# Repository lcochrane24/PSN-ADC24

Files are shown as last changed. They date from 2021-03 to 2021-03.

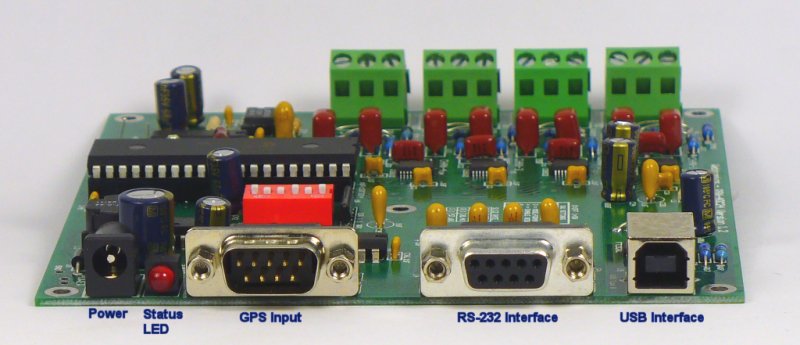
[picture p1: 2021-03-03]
html/adc24front.jpg

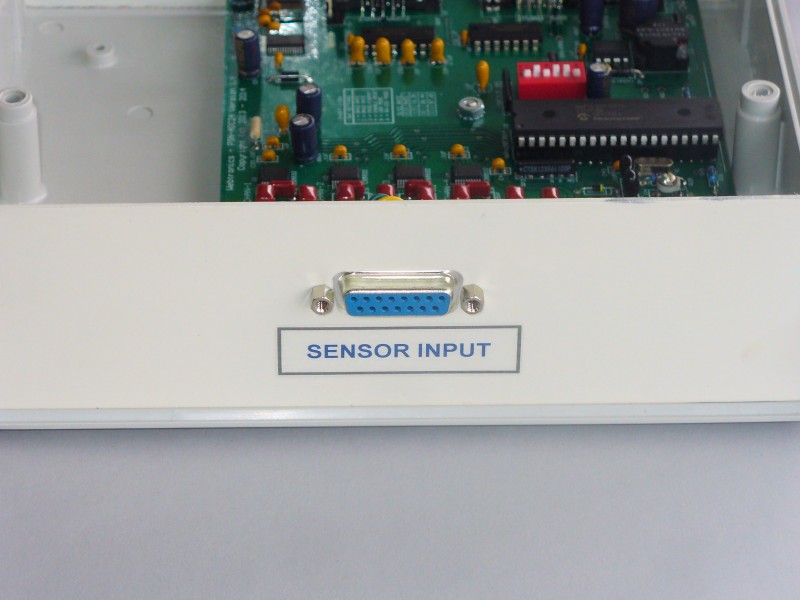
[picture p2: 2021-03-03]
html/adc24db15.jpg

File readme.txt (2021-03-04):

This folder contains the files needed to build the PSN-ADC24 4-Channel 24-Bit Analog to digital board. 
See https://www.seismicnet.com/psnadc24/ for more information. I am making this information available 
since they are no longer for sells. This is what is in each of the sub-folders.

BOM - The file sdr24adc_bom.txt is the bill of materials for the board.

gerber - Gerber files to make the PCB. The board is 4 layers with a size of 5.5 x 5.0 inches (13.97 x 12.7 cm ).

hexfiles - Contains the hex files that need to be flashed onto the DspPic CPU.

html - This is a copy of the PSN-ADC24 files on my web site https://www.seismicnet.com/psnadc24/

schematic - Schematics of the board.

src - Source code files.

build_info.txt - Information on how to build and test the board.

Please do not contact me directly regarding building this board. For support please use the PSNList Google group at
https://groups.google.com/g/psnlist

Thanks,
Larry Cochrane

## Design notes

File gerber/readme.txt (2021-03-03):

Board Name: Sdr24Adc17
Version 1.7

Layer Stack-up Sequence and polarity

Top Layer     Sdr24Adc17.GTL	POSITIVE
Inner Layer 1 Sdr24Adc17.G2	POSITIVE
Inner Layer 2 Sdr24Adc17.G1	POSITIVE
Bottom Layer  Sdr24Adc17.GBL    POSITIVE 

File Types:

Sdr24Adc17.GTL	Top Copper Layer
Sdr24Adc17.GBL  Bottom Copper Layer
Sdr24Adc17.G1   Inner Power  Layer
Sdr24Adc17.G2	Inner Ground Layer

Sdr24Adc17.GTS	Top Solder Mask
Sdr24Adc17.GBS	Bottom Solder Mask

Sdr24Adc17.GTO	Top Silkscreen

Sdr24Adc17.GPT	Top Pad Master
Sdr24Adc17.GPB  Bottom Pad Master
Sdr24Adc17.GTP	Top Paste Mask

Sdr24Adc17.GD1	Drill Drawing
Sdr24Adc17.GM4	Mechanical Drawing

Sdr24Adc17.DRL	NCDrill File
Sdr24Adc17.DRR	NCDrill File Report
Sdr24Adc17.txt	Excellon Drill File 

Note:

Please do not contact me directly regarding building this board. For support please use the PSNList Google group at:
https://groups.google.com/g/psnlist

Thanks,
Larry Cochrane

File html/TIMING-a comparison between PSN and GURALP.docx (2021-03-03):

Timing.

Comparison of arrival time of a specific seismic wave train as recorded by five instruments.

Using PSN and EchoPro equipment.

PSN [Larry Cochrane equipment] and the EchoPro [ES&S equipment].

PSN.

a) VolksMeter A horizontal displacement. located at TPSO. Uses internal Larry PCB.

b) VolksMeter B horizontal displacement. located at TPSO. Uses internal Larry PCB.

c) Wilmore 1 Second Vertical located at TPSO. Uses 24 bit Larry PCB

d) Sprengnether 20 Second Vertical located at TPSO. Uses 24 bit Larry PCB.

NOTE: The 24 bit Larry PCB is a 4 channel board, receiving both the Wilmore and the Sprengnether signal.

EchoPro.

e) Guralp CMG-6T-1 3 axis 1 Second to 100 Hz located at HMV1. Uses EchoPro digitizer.

NOTE: TPSO is located at 35.489 S 138.637 S. HMV1 is located 102 metres to the South of TPSO, so any difference in arrival time of a particular seismic wave train at these two stations, is of the order of no more than 0.02 seconds.

Seismic Wave Train

The seismic wave train used for timing, is the peak of the first big S wave arriving from the Strathalbyn quake of 2016-03-29 22:07.

Horizontal

VolksMeter A.

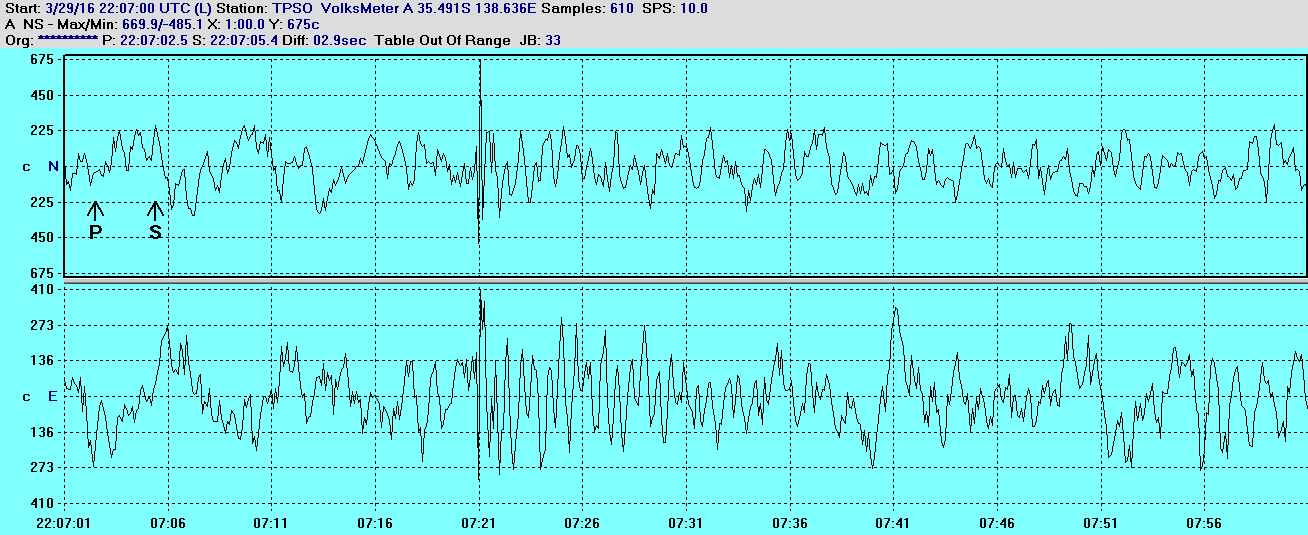
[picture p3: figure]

The peak of the first big S wave arrival time from VolksMeter A is 22:07:21.0 for both N/S and for E/W. Remember VolksMeter only records at 10 SPS.

VolksMeter B

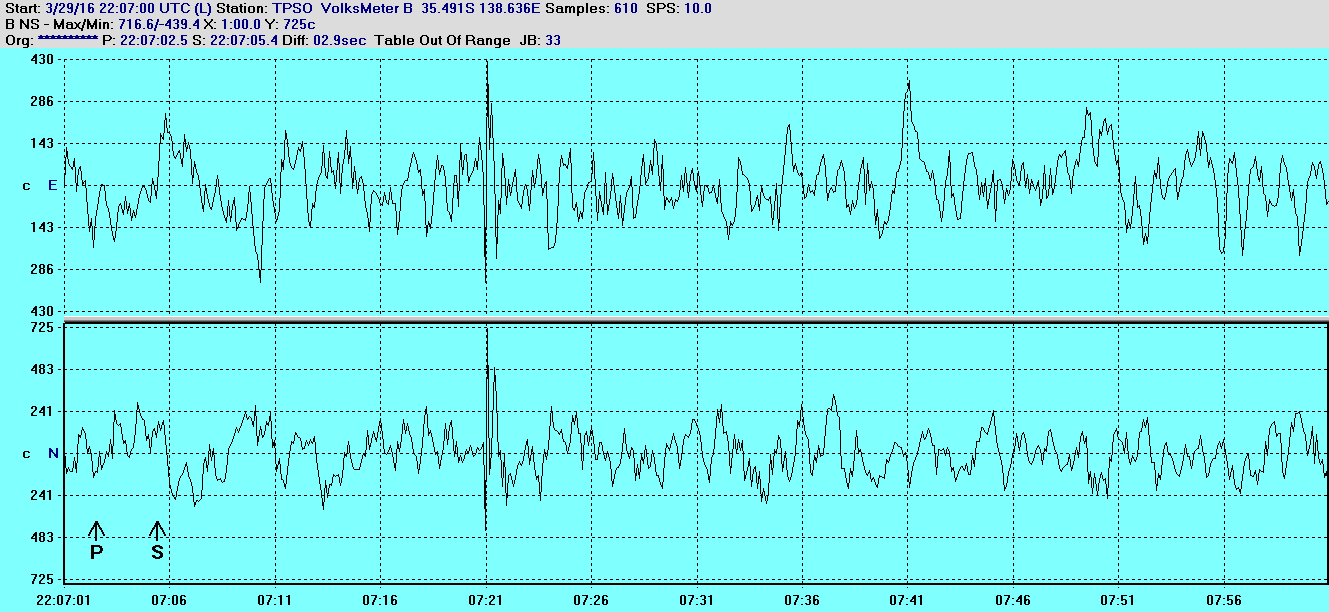
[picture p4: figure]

The peak of the first big S wave arrival time from VolksMeter B. Timing for both N/S and for E/W is 22:07:21.0.

Guralp

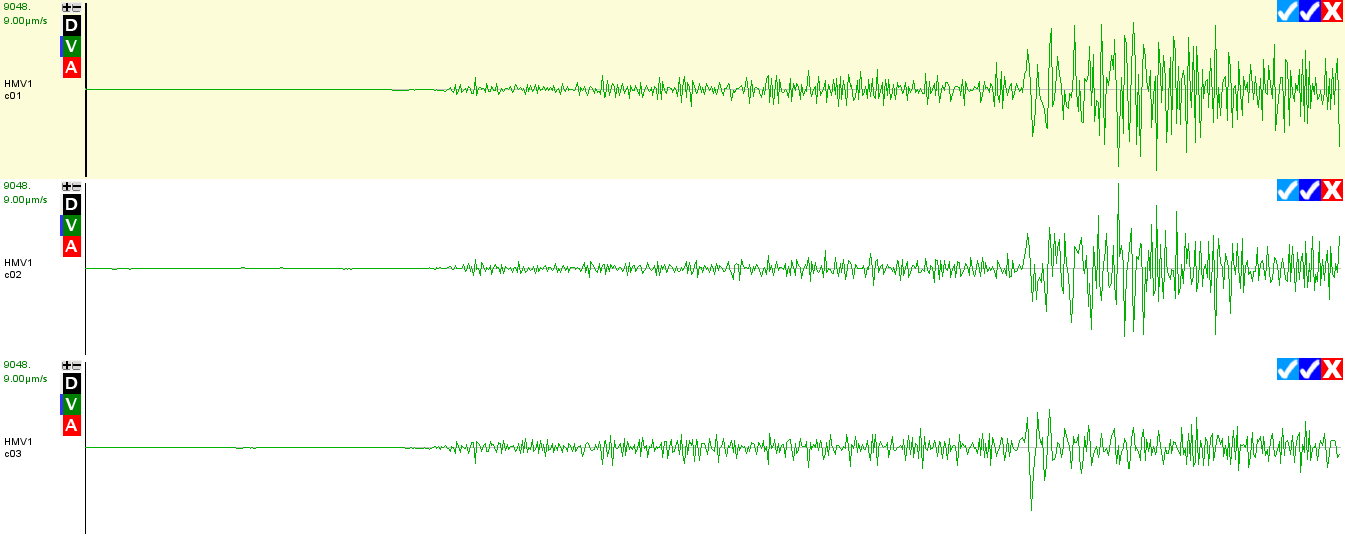
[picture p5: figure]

The peak of the first big S arrival time from the Guralp E/W is at 22:07:21.034, and for the N/S 22:07:21.034.

The peak of the first big S arrival time from the Guralp VERTICAL is 22:07:21.034.

That is all three axis from the Guralp show 22:07:21.034.

Vertical traces from Wilmore and Sprengnether shown on next page.

Vertical

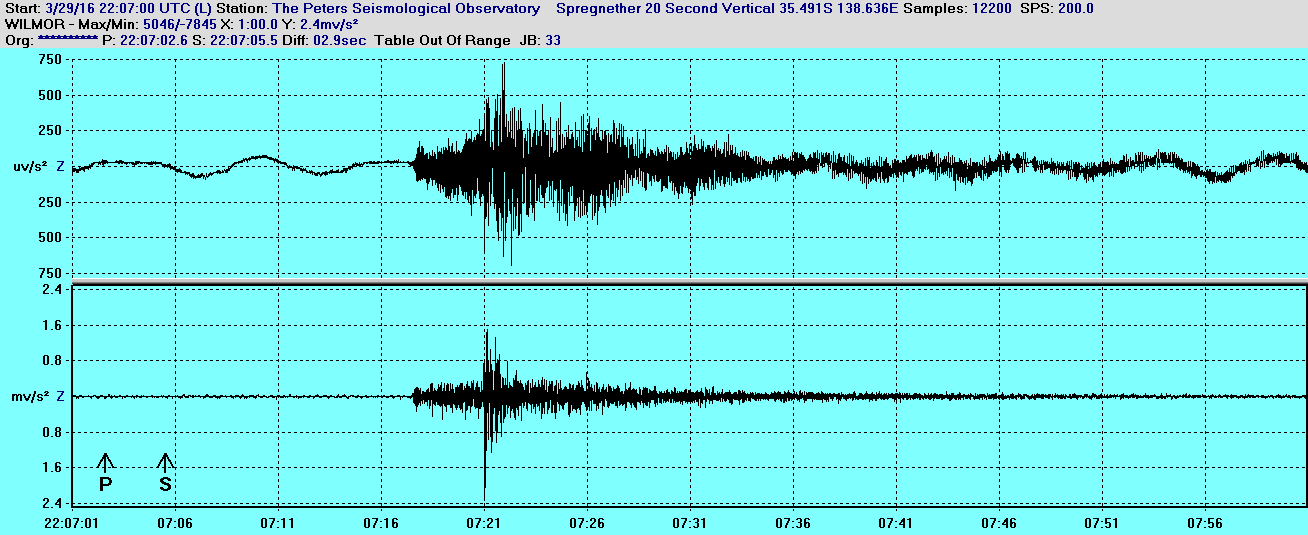
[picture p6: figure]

The top trace is the Sprengnether 20 Second Vertical which shows the peak of the first big S wave at 22:07:21.038

The lower trace is the Wilmore 1 Second vertical which shows the peak of the first big S wave at 22:07:21.042. Note both Wilmore and Sprengnether are both timed from the same 24 bit LARRY Board.

From the Guralp 3 axis trace previously, it shows a VERTICAL arrival at 22:07:21.034

Observed arrival time of the peak of the first big S wave.

a) VolksMeter A both N/S and E/W 22:07:21.0 10 SPS

b) VolksMeter B Both N/S and E/W 22:07:21.0 10 SPS

c) Wilmore Vertical 22:07:21.042. 200 SPS

d) Sprengnether Vertical 22:07:21.038 200 SPS

e) Guralp all three axis 22:07:21.034. 100 SPS

As can be seen there is good correlation in the timing between all 5 instruments.

And between all 9 traces.

Good correlation between the PSN equipment and the ES&S equipment.

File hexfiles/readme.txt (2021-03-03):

Files in this folder:

sdr24boot.hex - This is the bootloader for the DSPic30F3014 microcontroller. You must flash this bootloader first
                using a programer that can flash the 40 pin DSPic30F3014 part.

Sdr24AdcV25.hex - Once you have the bootload intalled place the chip into the ADC board and use the DspBoot.exe 
                  program to flash the firmware onto the CPU.
                  
DspBoot.exe - This Windows command line program is used to flash the firmware onto the microcontroller.

              Usage: DspBoot [ -p Port_Number ] [ -b Baud_Rate ] [ -t ] Hex_File
	      
	             Optional Parameters:
    	                -p Port Number 1 through 8 Default=1
    	                -b Baud Rate 9600, 19200, 38400, 57600 Default=38400
    	                -t Display Dspic CPU Type

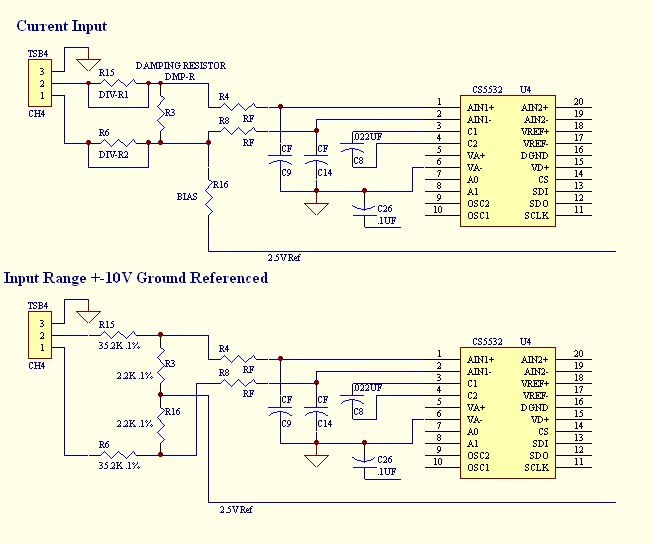
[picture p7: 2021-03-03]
html/diffInput_1.jpg

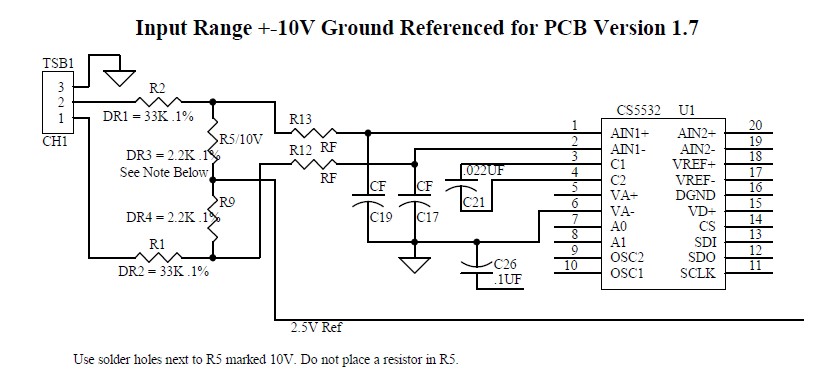
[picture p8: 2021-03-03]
html/Input10V.jpg

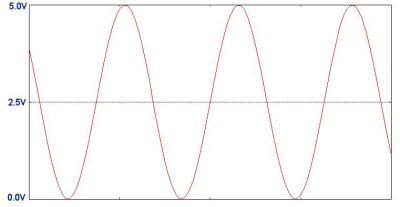
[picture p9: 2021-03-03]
html/inputrange.jpg

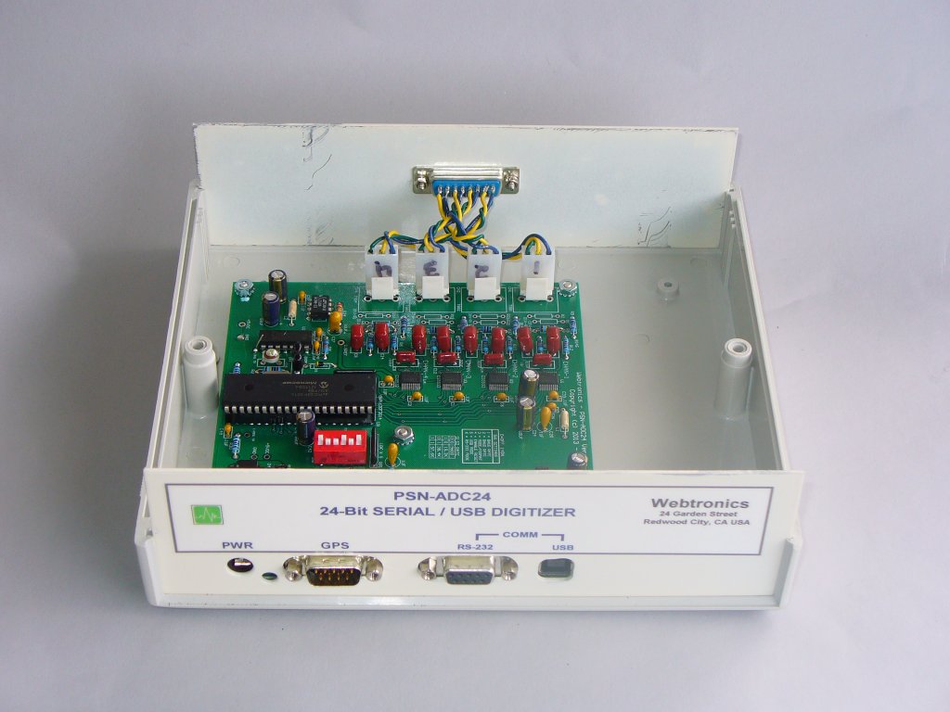
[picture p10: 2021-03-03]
html/adc24box.jpg

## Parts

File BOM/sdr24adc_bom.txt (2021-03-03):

BOM for PSN-ADC24 Board

Part Type,  Designator, 	Description     Package	    	Supplier(s)	                Notes
											LS = Lead Spacing in MM
Diodes
1N5819	    D1, D2, D4, D6	SCHOTTKY DIODE	DO-41	  	Jameco or Digi-Key
KV3901	    D3                  VAR CAP DIODE	DO-41	        eBay	       		Might be an obsolete part
LED	    D5			RED PCB LED	LS=2.5		Jameco PN 104248
 
Resistors
1K	    R30			1% MF 1/4W      axial0.4   	Digi-Key	
10K	    R17, R31		1% MF 1/4W      axial0.4   	Digi-Key
4.7K	    R7                  1% MF 1/4W      axial0.4   	Digi-Key
1.0M	    R29                 1% MF 1/4W      axial0.4	Digi-Key
1.0M	    R3, R5, R18, R27    1% MF 1/4W      axial0.4     	Digi-Key		DR3 Damping Resistor
2.2 OHM     R24			5% Carbon 1/4W  axial0.4	Jameco or Digi-Key	Jumper can be used here
33K	    R28			1% MF 1/4W      axial0.4     	Digi-Key
200K	    R9,  R14, R16, R21  1% MF 1/4W      axial0.4	Digi-Key		Bias Resistor
5.1K	    R4,  R8,  R10, R11  1% MF 1/4W      axial0.4	Digi-Key		RF Input LP Filter Resistor
5.1K	    R12, R13, R22, R23  1% MF 1/4W      axial0.4	Digi-Key		RF Input LP Filter Resistor
Not Used    R50, R51            1% MF 1/4W      axial0.4

10K X 5,    RP1, RP2		SIP6 5RES ARRAY LS=2.5x6	Digi-Key PN 770-61-R10KP

Coils
6.8UH	    L1, L2	        PWR FILTER COIL axial0.5	Digi-Key PN DN7691-ND   Can also use 3.3UH 
173UH	    L3			PWR COIL 540MA			Digi-Key PN TE2176-ND or TE2178-ND

Capacitors
0.1UF/50V   C1,  C2,   C4, C6	CAP CERAMIC	RAD0.1		Digi-Key PN 478-3192-ND
0.1UF/50V   C10, C13, C18, C23, 50V 20% Radial
0.1UF/50V   C26, C33, C36, C37, 
0.1UF/50V   C39, C40, C41, C43, 
0.1UF/50V   C49, C50
0.022UF/50V C8, C12, C21, C31   5% FILM CAP    	RAD0.2		Digi-Key PN P4517-ND    Panasonic ECQ-V1H223JL
1.0UF/25V,  C20, C22, C28, C30	TANTALUM	RAD0.1	  	Jameco PN 545588
1.0UF/25V   C34, C35
220PF/500V  C44			SILVER MICA 	LS=5.9		Digi-Key PN 338-1046-ND CDE CD15FD221JO3 
10UF/20V    C27			TANTALUM 10%    LS=2.5		Jameco PN 545633
100UF/50V"  C47			ALUM 20% FC CAP LS=5.0		Digi-Key PN P10323-ND	Panasonic EEU-FC1H101		
68UF/35V    C3,  C5,  C24, C42	ALUM 20% FC CAP LS=2.5		Digi-Key PN P10292-ND   Panasonic EEU-FC1V680
68UF/35V    C38, C45, C48 
TRIM CAP    C46		        VAR CAP 9PF-50PF LS=5.0		Jameco PN 136979	
.68UF/63V   C9,  C14, C15, C16	FILM 5% RADIAL	LS=5.0		Digi-Key PN 399-6030-ND Kemet R82DC3680AA60J
.68UF/63V   C17, C19, C25, C32

Crystal
4.9152MHZ   Y1			20PF	        HC49/US		Digi-Key PN X1049-ND 

Switch
6-POS DIP   SW1			SLIDE DIP SWITCH 12-PIN		Jameco PN 38826

IC Chips
CS5532ASZ   U1, U2, U3, U4	CIRRUS ADC CHIP	SOP20		Digi-Key PN 598-1112-5-ND 
74HC14	    U10			HEX INVERTER    DIP14		Digi-Key or Jameco
DS14C89	    U8			RS-232 RECV     DIP14		Digi-Key PN DS14C89AN/NOPB-ND
MAX232	    U5			RS-232 TX/RX    DIP16		Digi-Key or Jameco
DSPic30F3014 U9			MicoChip CPU    DIP40		Digi-Key PN DSPIC30F301430/P-ND 
SOCKET FOR  U9			40PIN SOCKET	DIP40		Digi-Key or Jameco
FT232RL	    U6			USB INTERFACE   SOP28		Digi-Key PN 768-1007-1-ND
LT1019-2.5  U7			2.5V REF IC     DIP8		Digi-Key PN LT1019CN8-2.5#PBF-ND
LM2594-5    U11			IC REG BUCK 5V	DIP8		Digi-Key PN LM2594N-5.0/NOPB-ND 

Connectors
PWR CON     J2			2.1MM DC PWR JACK		Jameco PN 137673
DB9M        J3			DB9 MALE RT    .318		Jameco PN 104943
DB9F        J4			DB9 FEMALE RT  .318		Jameco PN 104952
USB Type B  J5			USB CONN			Jameco PN 230958 or 2096245 

INPUT CONN  TSB1,TSB2,TSB3,TSB4 3-TERMINAL SCREW BLOCK		Jameco PN 161059
				or 3 POS 3.96 (.156) MOLEX	
				HEADER 				Jameco PN 879887

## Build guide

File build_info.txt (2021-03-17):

Building and testing the PSN-ADC24 board.

1. Solder the parts onto the board. Use a socket for the dsPIC30F3014 microcontroller. You will need to deal with 5 SMD parts, the 4 ADC chips and the USB interface IC. A bill of materials can be found in the BOM folder.

2. Before placing the dsPIC30F3014 into the socket you will need to flash the bootloader onto the chip. This is done with a programmer that can flash 40-pin dsPIC30F3014 parts. I use one made by ME Labs, Inc. I have their older serial version but their U2 USB Programmer should work. The file to flash is sdr24boot.hex that can be found in hexfiles folder.

3. Once you have the bootloader loaded onto the CPU you can place it into the 40-pin socket and power up the board. You will need a 7VDC to 20VDC power supply. A 12VDC power supply with 500ma or more current is perfect to run the board.

4. Set the 6 position switch to the following: 
   SW1 = OFF and SW2 = ON - This will set the baud rate to 38.4k
   SW3 = OFF              - This switch is not used
   SW4 = ON               - This must be on so the host computer can reset the board.
   SW5 = ON and SW6 = OFF - USB Interface Mode
   or
   SW5 = OFF and SW6 = ON - RS-232 Interface Mode
   Note: SW5 and SW6 can not be both on at the same time!

5. When you apply power for the first time the LED should come on. This indicates that the microcontroller is running and ready to receive the firmware.

6. Use the DspBoot.exe program, this can be found in the hexfiles folder, to flash the firmware onto the dsPIC CPU. You will need to run the DspBoot program using a command line window. Make sure that you have SW5 and SW6 set to the correct positions depending on if you will be using the USB or RS-232 interface. This file Sdr24AdcV25.hex is the current firmware for the board. The DspBoot program only needs three input parameters, -p, the port number and the firmware file. 
    Example: DspBoot -p 1 Sdr24AdcV25.hex

7. If the flashing of the firmware worked correctly the LED should start to blink after DspBoot toggles the reset line.

8. Before running the board you should set the crystal oscillator to 4.915200MHz +- a few Hz. This should be done with an accurate frequency counter. Use the 4.9 TP test point located near the 74HC14 U10 chip to monitor the frequency and adjust the variable capacitor C46 to the correct frequency.

The board should now be ready to use with WinSDR or my PsnAdSend earthworm module.

If you have any questions please use the PSNList Google group at 
https://groups.google.com/g/psnlist for support.

Good luck,
-Larry Cochrane

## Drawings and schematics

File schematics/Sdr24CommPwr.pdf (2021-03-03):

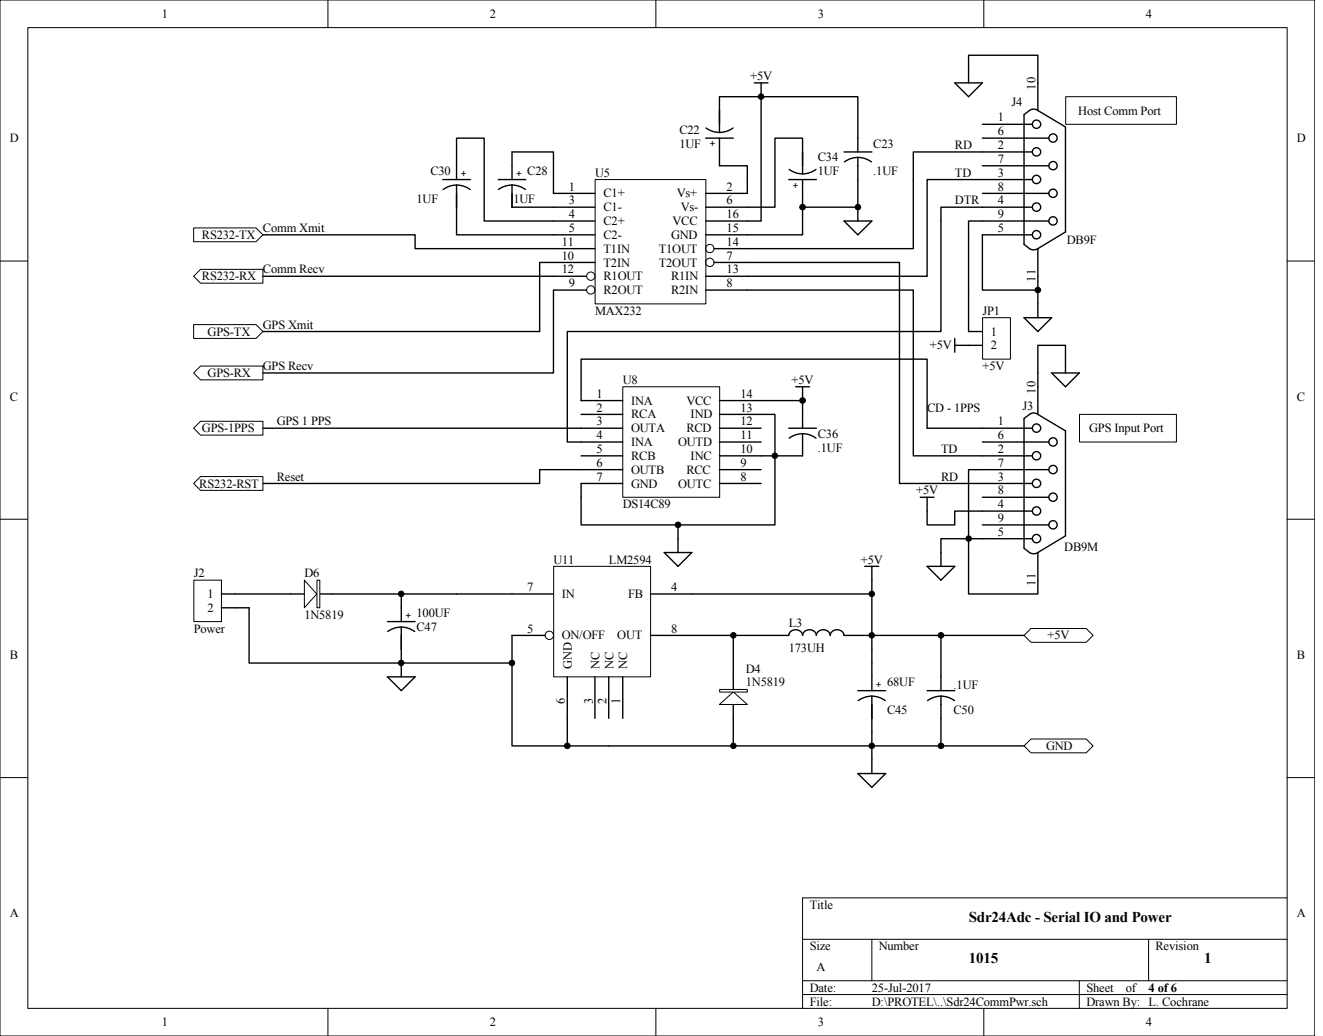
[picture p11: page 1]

Sdr24Adc - Serial IO and Power

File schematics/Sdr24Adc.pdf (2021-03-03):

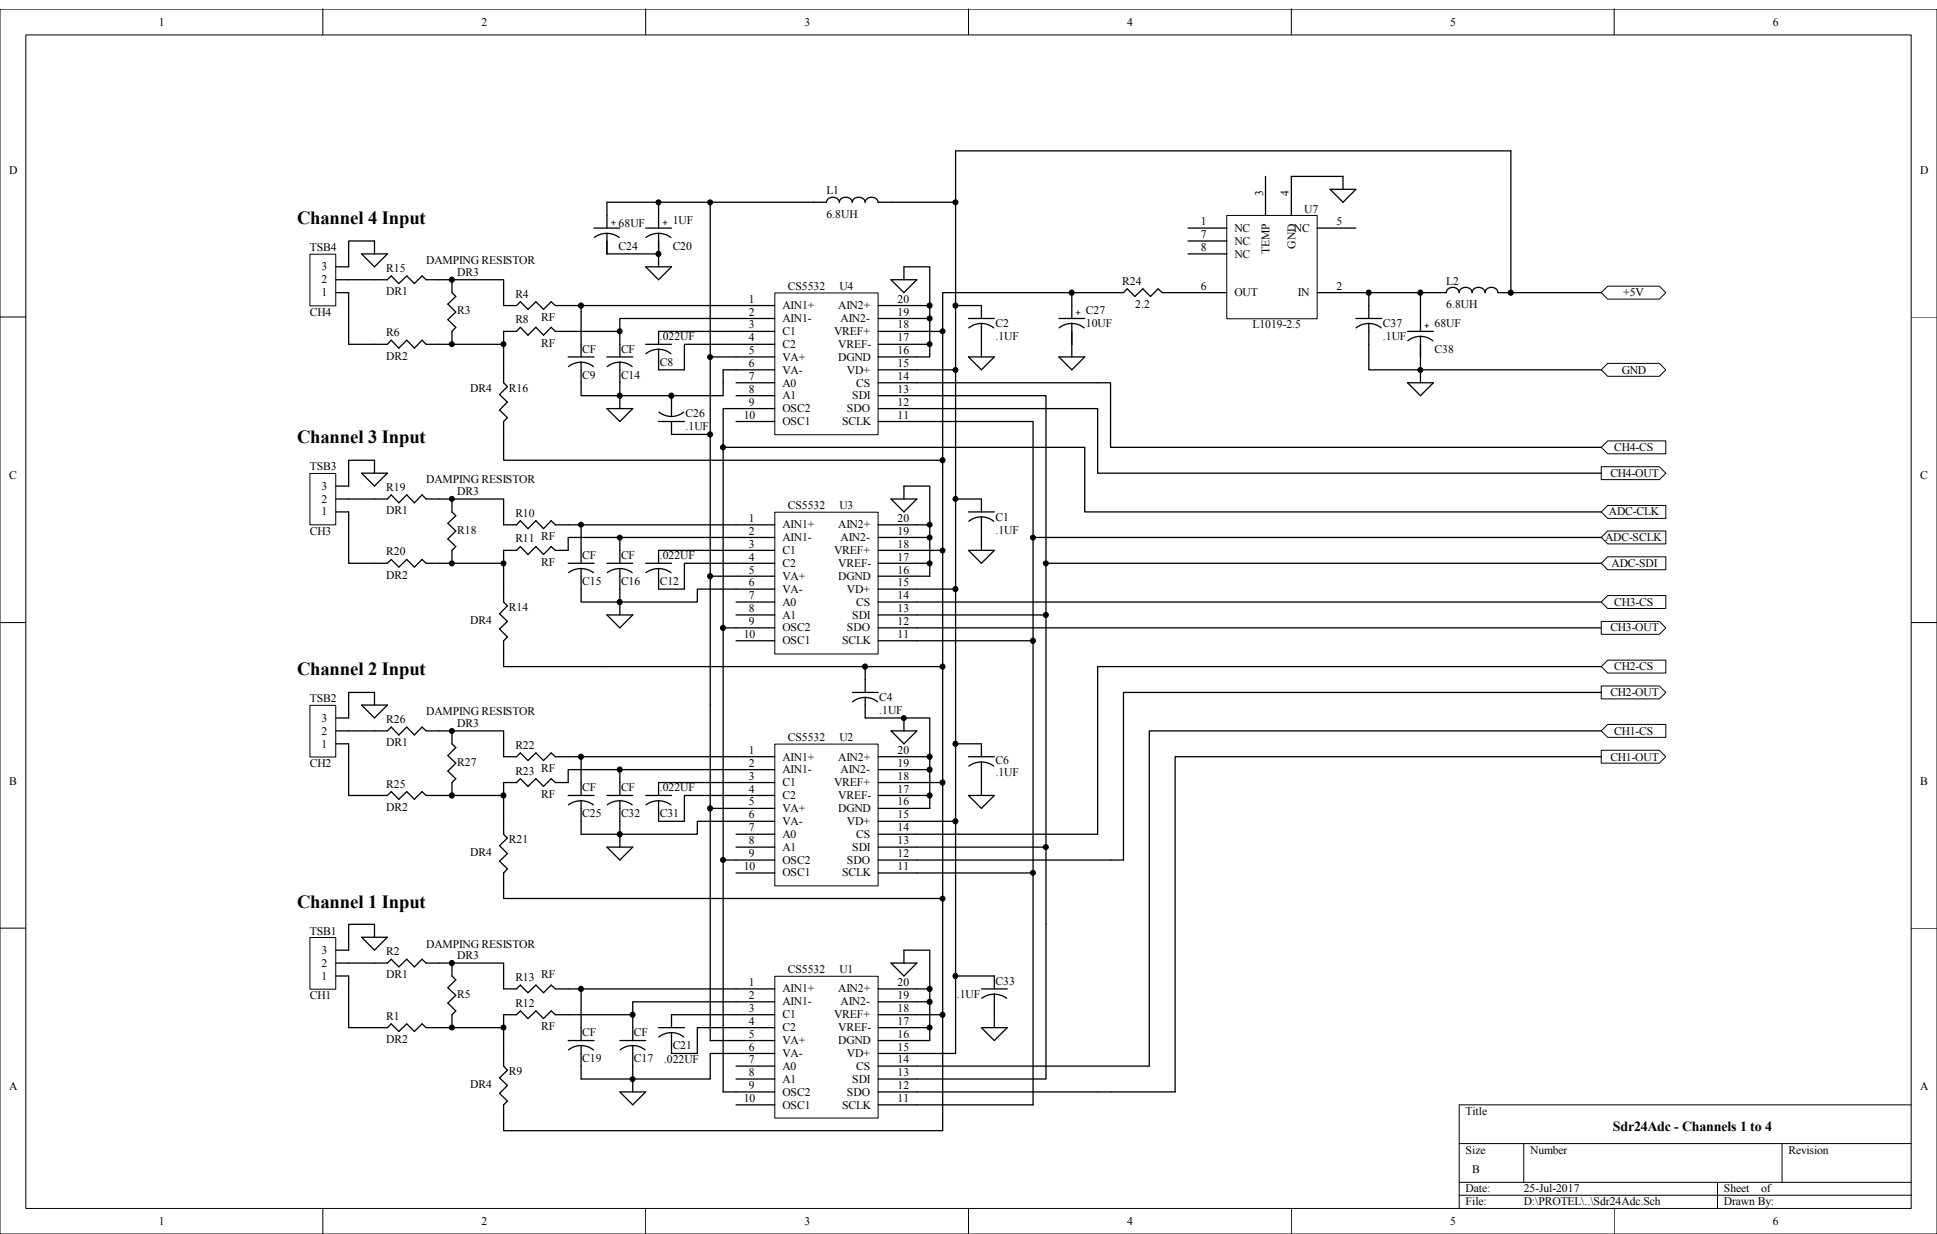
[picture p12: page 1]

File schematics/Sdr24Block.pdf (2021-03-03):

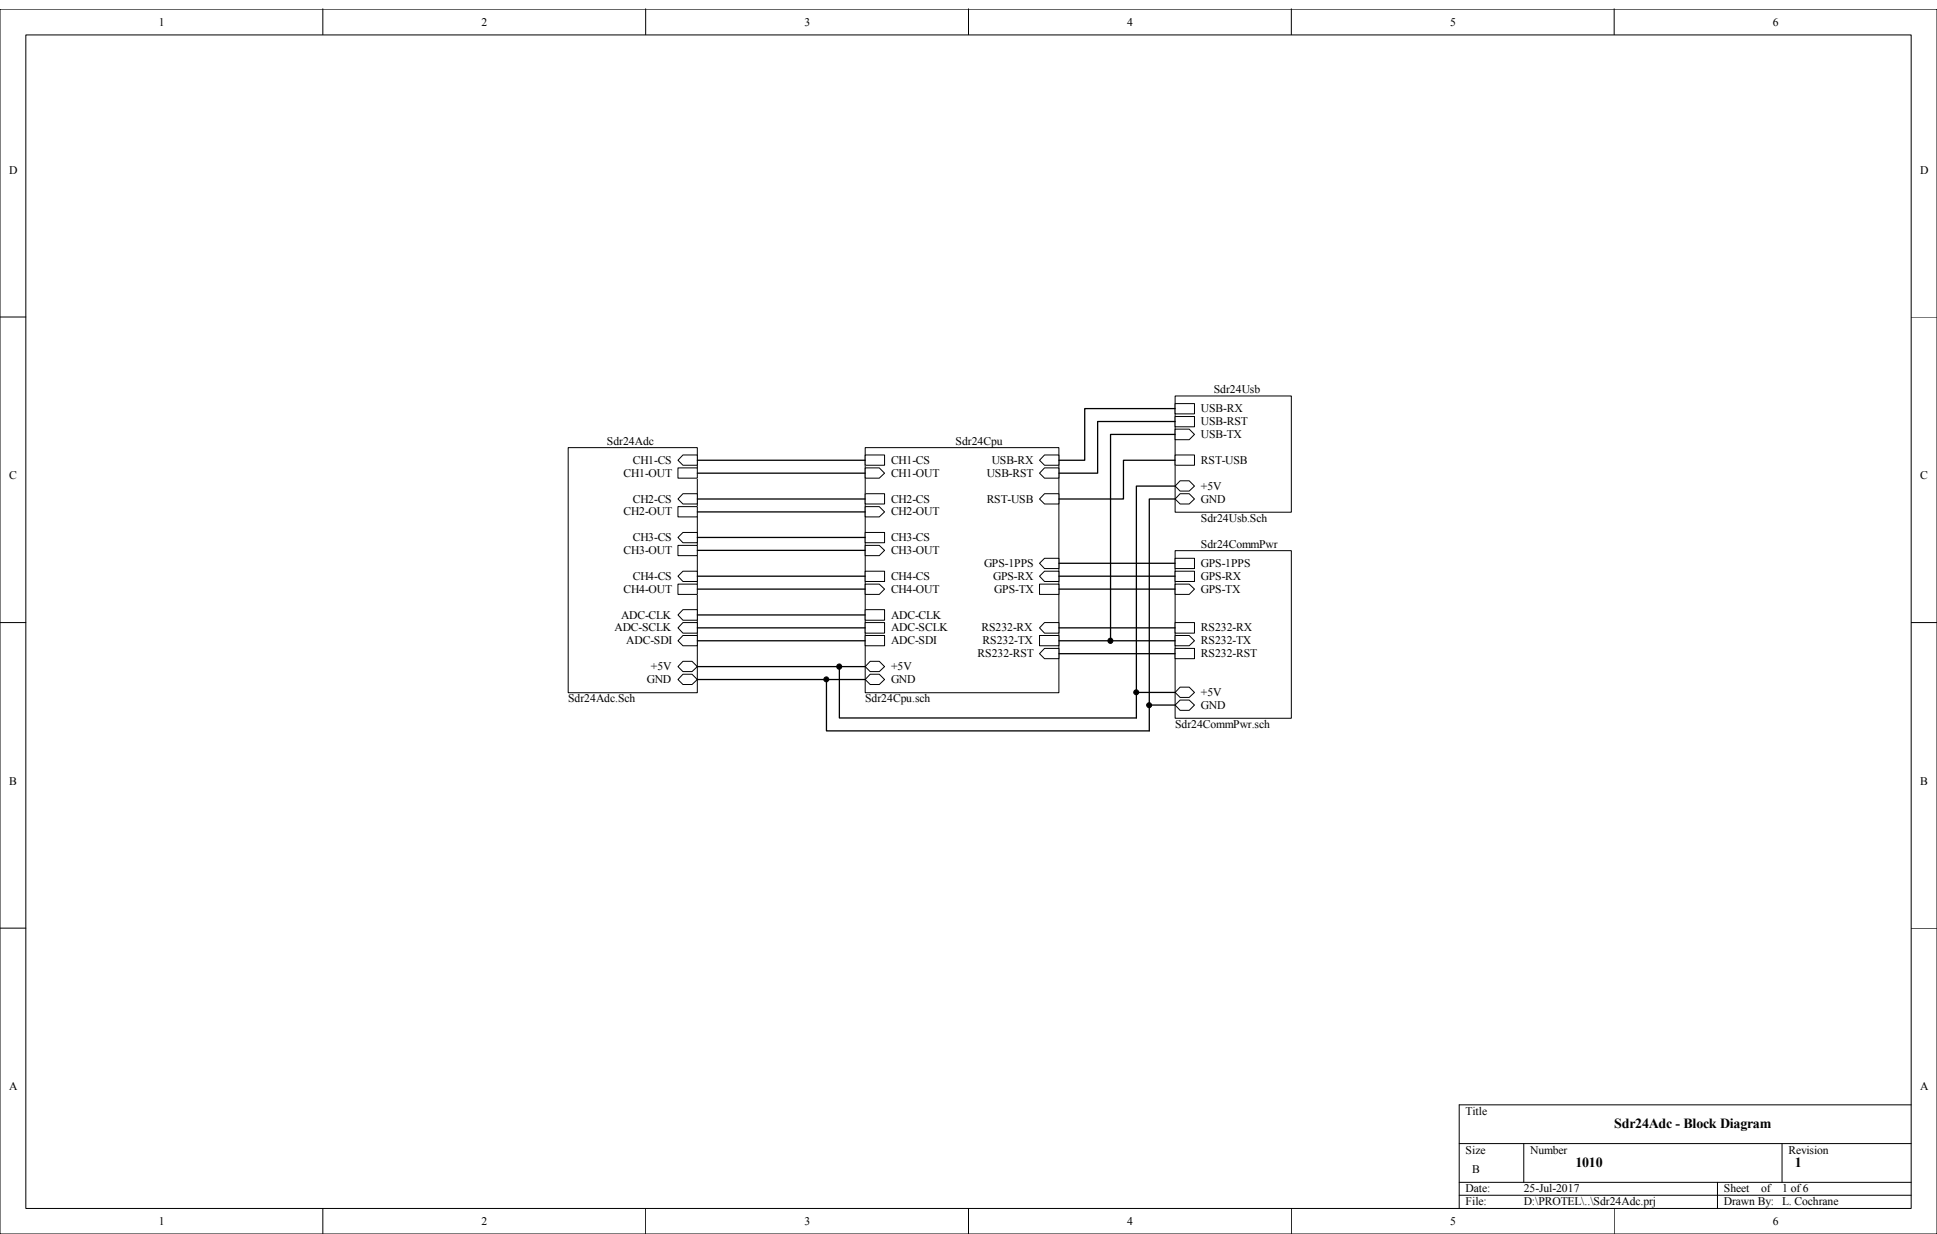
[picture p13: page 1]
Title; Size; Number; Revision; Date:; 25-Jul-2017; Sheet of; File:; D:\PROTEL\..\Sdr24Adc.prj; Drawn By:; ADC-SDI; CH1-OUT; ADC-SCLK; CH2-CS CH2-OUT; CH3-CS CH3-OUT; ADC-CLK; GND; CH4-CS CH4-OUT; Sdr24Adc; Sdr24Adc.Sch; RS232-RST; CH3-OUT; CH2-OUT; GPS-TX; GPS-RX; GPS-1PPS; USB-RX USB-RST; ADC-SCLK ADC-SDI; CH4-OUT; RST-USB; Sdr24Cpu; Sdr24Cpu.sch; RS232-TX RS232-RST; GPS-1PPS GPS-RX GPS-TX; Sdr24CommPwr; Sdr24CommPwr.sch; USB-RX; USB-TX; USB-RST; +5V GND; Sdr24Usb; Sdr24Usb.Sch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

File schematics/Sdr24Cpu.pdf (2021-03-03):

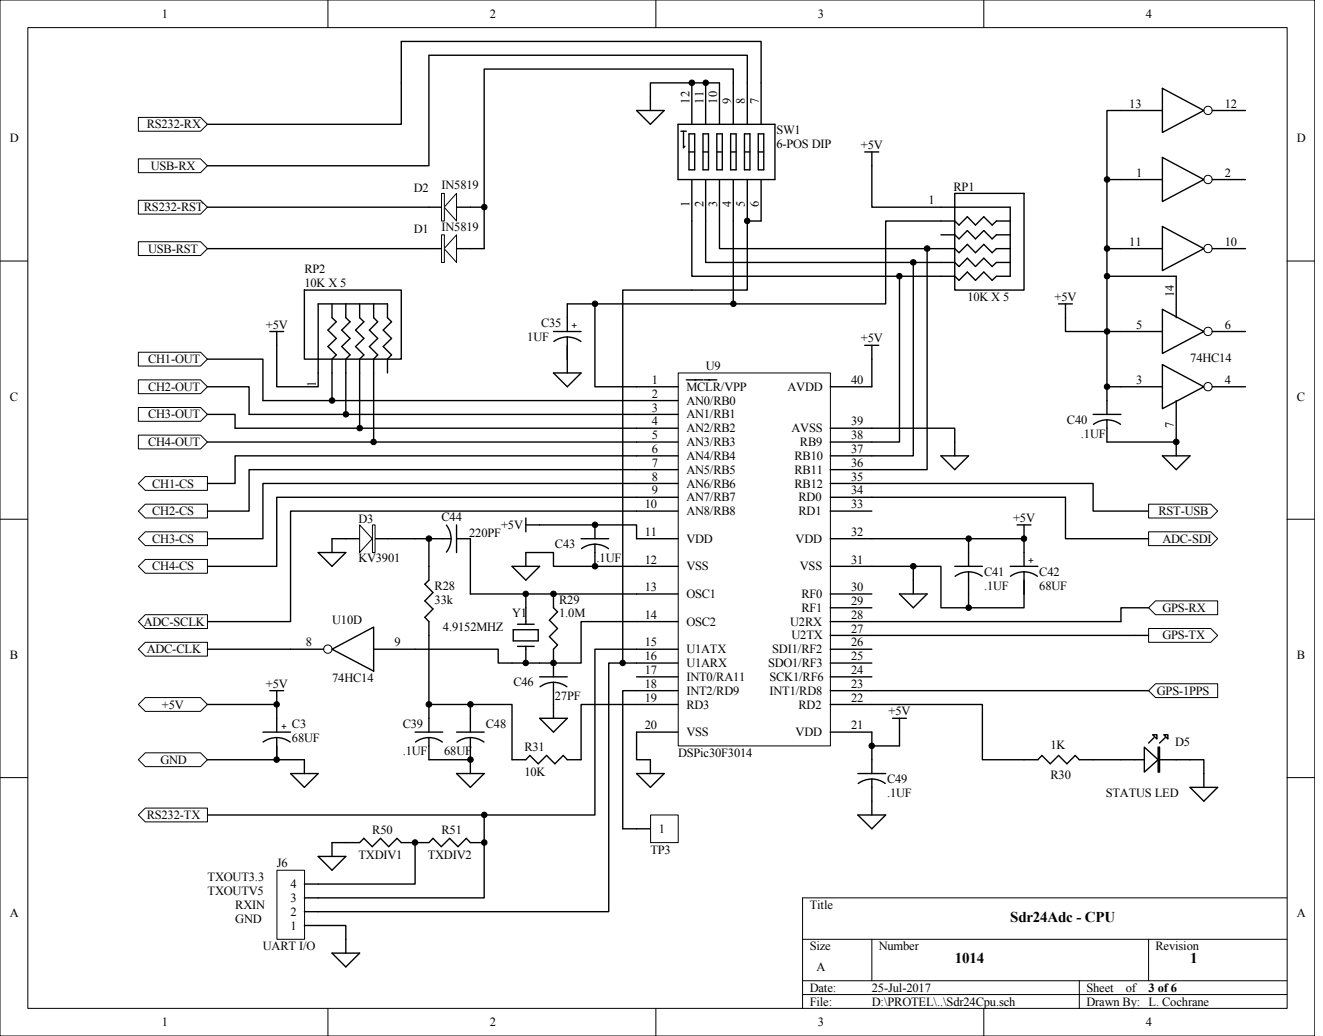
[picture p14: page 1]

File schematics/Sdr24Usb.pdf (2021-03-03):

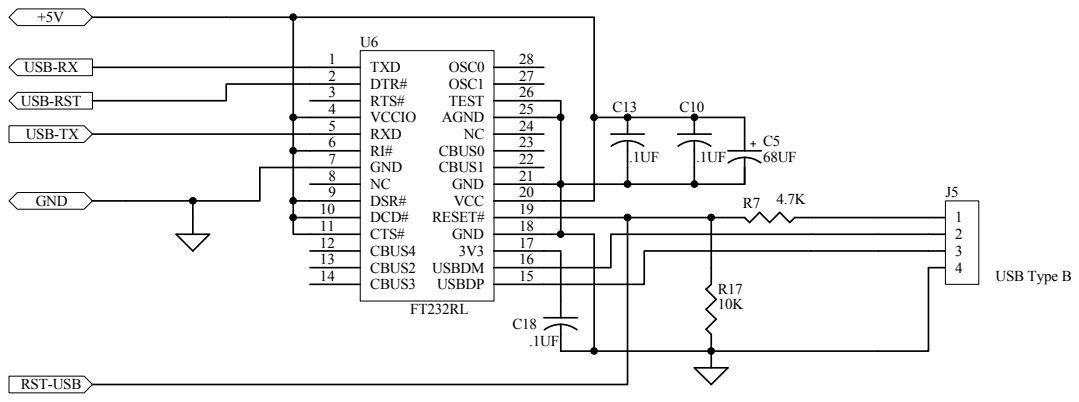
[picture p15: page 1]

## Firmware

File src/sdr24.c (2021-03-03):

/* sdr24.c */

#ifdef CPU4013
#include "p30F4013.h"
#else
#include "p30F3014.h"
#endif

_FOSC( CSW_FSCM_OFF & XT_PLL8 );
_FWDT(WDT_OFF & WDTPSA_64 & WDTPSB_4);
_FBORPOR( PBOR_ON & BORV_42 & PWRT_16 & MCLR_EN );
_FGS( CODE_PROT_OFF );

#include <uart.h>
#include <stdio.h>
#include <stdlib.h>
#include "sdr24.h"

BYTE ppsLowHiFlag, setGpsTimeFlag, outBuffer, samplesPerPacket;
BYTE newInData, sendLog, exitLoop, sendStatus, goodConfig;
BYTE ppsHiToLowFlag, ledPPS, newCommandFlag, checkErr, sendTime;
BYTE echoMode, newEchoChr, resetTime;
BYTE sendAckFlag, packetsPerSec, sendAdcInfoFlag, calcFlag;

BYTE inBuffer[IN_BUFFER_SIZE], inBuffQueue[ IN_BUFFER_SIZE ];
volatile BYTE *inPtrQue;
 
BYTE dataPacket[DATA_PACKET_LEN], dataPacket1[DATA_PACKET_LEN], auxPacket[AUX_PACKET_LEN], hdrStr[4], *txOutPtr;
BYTE *adDataPtr;

char gpsInBuffer[ GPS_BUFFER_LEN ], gpsInQueue[ GPS_IN_QUEUE], lastGpsChar;
WORD gpsInCount, gpsQueueInCount, gpsQueueOutCount, newGpsData;

WORD secTick, secTickValue, secOffValue, gpsTimer;
ULONG packetID, gpsTimeOfDay, timeTick, ppsTick, timeStamp;

Sdr24DataHdr *currHdr;

WORD txOutCount, sampleDataLen, sampleOffset;

BYTE sampleCount, numChannels, timeRefType, noWaitFlag, goodChanFlags;
WORD spsRate, noDataCounter;

Sdr24ConfigInfo config;
BYTE baudSwitch, modeSwitch;

BYTE gpsHour, gpsMin, gpsSec, sendHour, sendMin, sendSec;
BYTE gpsSatNum, gpsWaitLines, gpsMonth, gpsDay, gpsYear;
char gpsLockChar, ggaLockChar, needTimeFlag;

volatile BYTE hdrState, commTimer, inDataLen, inPacketLen;
BYTE inSum, echoChar;

BYTE gpsSendState, gpsBadCount, gpsSendWait, gpsSendLine, gpsLineLen;
BYTE gpsReset, gpsOutLine[GPS_OUT_LEN], *tx2OutPtr, tx2OutCount;

BYTE gpsOutBuffer[ MAX_GPS_OUT_LEN+sizeof(PreHdr)+4 ], gpsOutBuffer1[ MAX_GPS_OUT_LEN+sizeof(PreHdr)+4 ];
BYTE gpsOutSendLen, gpsOutLen, gpsOutSum, *gpsOutBuffPtr, *gpsOutSendPtr, skipGpsSend;
BYTE gpsOutIdx, sendGpsData, numConverters, numChanError, spsError, errWait;

char logStr[AUX_PACKET_LEN];

SendTimeInfo sendTimeInfo;

WORD vcoOnTime, vcoOffTime, vcoTime, newVcoOnTime, newVcoOffTime;
BYTE vcoPinOn, watchdogCheck, noDataFlag;

AdcGainOffset gainOffsets[ MAX_CHANNELS ];

BYTE restartFlag;
WORD notRdyCount;

#include "sdr24utils.c"
#include "sdr24gps.c"
#include "sdr24int.c"
#include "sdr24adc.c"

int main()
{
	Init();
	restartFlag = 0;
	notRdyCount = 0;
			
LoopIn:
	
	Restart();

	restartFlag = 1;
	
	while( 1 )  {
		numConverters = InitConverters();
		if( !numConverters )  {
			strcpy( logStr, "No Converters");
			SendLogString();
			DelayMs( 100 );
			goto LoopIn;
		}
		
		if( noWaitFlag )  {
			noWaitFlag = 0;
			NewConfig();
		}
		else
			WaitForConfig();
		
		CalcAllAdc();
		
		StartAllCS5532();
				
		exitLoop = 0;

		while( !exitLoop )  {

			if( IsCS5532DataRdy() )  {
				NewSample();
				notRdyCount = 0;
			}
			else if( ++notRdyCount > 50000 )  {
				notRdyCount = 0;
				strcpy( logStr, "ADC Not Rdy");
				sendLog = 1;
			}
				
			if( newCommandFlag )  {
				newCommandFlag = 0;
				noDataCounter = 0;
				noDataFlag = 0;
				NewCommand();
				continue;
			}
				
			if( timeRefType )  {
				if( GpsCommCheck() )  {
					NewGpsTimeNMEA();
					continue;
				}		
				else if( gpsSendState )
					CheckSendGps();
			}
		
			if( !txOutCount )  {
				if( restartFlag )  {
					restartFlag = 0;
					strcpy( logStr, "Restart Flag");
					sendLog = 1;
				}
				if( sendTime )
					SendTime();
				else if( sendStatus ) 
					SendStats();
				else if( sendLog )
					SendLogString();
				else if( sendAckFlag )
					SendAck();
				else if( sendAdcInfoFlag )  {
					StopAllCS5532();
					if( calcFlag )  {
						CalcAllAdc();
						calcFlag = 0;	
					}
					GetAdcGainOffsets();
					StartAllCS5532();
					SendAdcInfo();
				}
			}
		}
	}
	
	goto LoopIn;
}

void SendError()
{
	if( errWait )
		--errWait;
	if( !errWait )  {
		if( numChanError )
			strcpy( logStr, "Config Error: Num Converters");
		else if( spsError )
			strcpy( logStr, "Config Error: Wrong SPS");
		else
			strcpy( logStr, "Config Error" );
		SendLogString();
		errWait = 10;
	}
	sampleCount = 0;
	sampleDataLen = 0;
}

void NewSample()
{
	ClrWdt();
	
	if( !sampleCount )
		MakeHdr();
		
	TEST_PIN = 1;
	ReadCS5532DataAll();
	TEST_PIN = 0;
	
	if( ++sampleCount >= samplesPerPacket )  {
		if( spsError || numChanError )
			SendError();
		else  {
			SendDataPacket();
			Check100Ms();
		}
	}
}

void MakeHdr()
{
	if( outBuffer )  {
		currHdr = (Sdr24DataHdr *)&dataPacket1[ sizeof( PreHdr ) ];
		adDataPtr = (BYTE *)( (BYTE *)&dataPacket1[ sizeof( PreHdr ) + sizeof( Sdr24DataHdr ) ] );
	}
	else  {
		currHdr = (Sdr24DataHdr *)&dataPacket[ sizeof( PreHdr ) ];
		adDataPtr = (BYTE *)( (BYTE *)&dataPacket[ sizeof( PreHdr ) + sizeof( Sdr24DataHdr ) ] );
	}
	sampleDataLen = 0;
	IEC0bits.T1IE = 0;
	currHdr->sampleTick = timeTick;
	currHdr->ppsTick = ppsTick;
	IEC0bits.T1IE = 1;
	currHdr->gpsMonth = gpsMonth;
	currHdr->gpsDay = gpsDay;
	currHdr->gpsYear = gpsYear;
	currHdr->gpsTOD = gpsTimeOfDay;
	currHdr->gpsSatNum = gpsSatNum;
	currHdr->gpsLockSts = gpsLockChar;
	currHdr->packetID = packetID + 1;
	currHdr->loopError = 0;
	currHdr->notUsed = 0;
}

void SendDataPacket()
{
	PreHdr *phdr;
	BYTE sum;
	WORD len;
		
	while( XmitCount() );
	
	len = sampleDataLen + sizeof( Sdr24DataHdr );
		
	if( outBuffer )  {
		memcpy( dataPacket1, hdrStr, 4 );
		phdr = (PreHdr *)dataPacket1;
		phdr->len = len + 1;			// one more for checksum
		phdr->type = 'D';
		phdr->flags = 0xc0;
		sum = CalcChecksum( &dataPacket1[ 4 ], len + 4 );
		dataPacket1[ len + sizeof(PreHdr) ] = sum; 
		txOutPtr = dataPacket1;
		outBuffer = 0;
	}
	else  {
		memcpy( dataPacket, hdrStr, 4 );
		phdr = (PreHdr *)dataPacket;
		phdr->len = len + 1;			// one more for checksum
		phdr->type = 'D';
		phdr->flags = 0xc0;
		sum = CalcChecksum( &dataPacket[ 4 ], len + 4 );
		dataPacket[ len + sizeof(PreHdr) ] = sum; 
		txOutPtr = dataPacket;
		outBuffer = 1;
	}
	txOutCount = len + sizeof( PreHdr ) + 1;	// one more for the checksum
	SendHost();
	sampleCount = 0;
	sampleDataLen = 0;
	++packetID;
}

void Check100Ms()
{
	if( gpsSendWait )
		--gpsSendWait;
		
	if( hdrState && ( ++commTimer >= 30 ) )  {
		hdrState = 0;
		strcpy( logStr, "Input Comm Timeout");
		sendLog = 1;
	}
	if( checkErr )  {
		checkErr = 0;
		strcpy( logStr, "Input Checksum Error");
		sendLog = 1;
	}
		
	if( watchdogCheck && ( ++noDataCounter >= NO_HOST_DATA_TIMER ) )  {
		noWaitFlag = 0;
		exitLoop = noDataFlag = 1;
		Restart();
	}
}

void NewConfig()
{
	while( XmitCount() );
	
	IFS0bits.U1RXIF = 0;		/* disable interrupts */
    IFS0bits.U1TXIF = 0;
	IFS1bits.U2RXIF = 0;
    IFS1bits.U2TXIF = 0;
	IEC0bits.T1IE = 0;
	
	memcpy( &config, &inBuffer[1], sizeof( Sdr24ConfigInfo ) );
	
	numChannels = config.numChannels;
	if( numChannels > numConverters )  {
		numChannels = numConverters;
		numChanError = 1;
	}
	else
		numChanError = 0;
	
	timeRefType = config.timeRefType;
	timeTick = config.timeTick;
	
	if( config.flags & FG_PPS_HIGH_TO_LOW )
		ppsHiToLowFlag = 1;
	else
		ppsHiToLowFlag = 0;

	spsRate = config.sps;
	if( !TestSampleRate( spsRate ) )  {
		spsError = 1;
		spsRate = 50;
	}	
	
	packetsPerSec = GetPacketsPerSec( spsRate );
	samplesPerPacket = spsRate / packetsPerSec;
	sampleOffset = numChannels * 3;
	
	if( config.flags & FG_DISABLE_LED )
		ledPPS = 0;
	else
		ledPPS = 1;
	
	if( config.flags & FG_WATCHDOG_CHECK )  {
		watchdogCheck = 1;
		RCONbits.SWDTEN = 1;
	}
	else  {
		watchdogCheck = 0;
		RCONbits.SWDTEN = 0;
	}
	vcoOnTime = config.vcoOnTime;
	vcoTime = vcoOffTime = config.vcoOffTime;
	vcoPinOn = 0;
	newVcoOnTime = 0;
	newVcoOffTime = 0;
	VCO_OUT = 0;
	
	goodConfig = 1;
	exitLoop = 0;
	
	Restart();
}

void NewCommand()
{
	char cmd;
	
	cmd = inBuffer[0];
	if( cmd == 'T' )
		SetTimeInfo();
	else if( cmd == 'D' )
		SendTimeDiff();
	else if( cmd == 't' )  {
		setGpsTimeFlag = 1;
		resetTime = 0;
	}
	else if( cmd == 'i' )  {
		setGpsTimeFlag = 1;
		resetTime = 1;
	}
	else if( cmd == 'd' )  {
		SetTimeDiff();
		sendAckFlag = 1;
	}
	else if( cmd == 'S' )
		sendStatus = 1;
	else if( cmd == 'x')  {
		noWaitFlag = 0;
		exitLoop = 1;
	}
	else if( cmd == 'C' )  {
		exitLoop = noWaitFlag = 1;
	}
	else if( cmd == 'g' )  {
		gpsReset = 1;
		gpsSendState = 1;
		gpsSendWait = 0;
	}
	else if( cmd == 'G' )  {
		gpsSendState = 1;
		gpsSendWait = 0;
	}
	else if( cmd == 'E' )  {
		EchoGps();
		exitLoop = 1;
	}
	else if( cmd == 'b' )  {
		GotoBootLdr();
	}
	else if( cmd == 'P' && !sendGpsData )  {
		if( timeRefType == TIME_SDR24_4800 || timeRefType == TIME_SDR24_9600 )  {
			sendGpsData = 1;
		}
		else  {
			if( timeRefType == TIME_SDR24_SKG )
				gpsReset = 1;
			sendGpsData = gpsSendState = 1;
			skipGpsSend = 3;
		}
		ClearGpsOut();
	}
	else if( cmd == 'p' && sendGpsData )  {
		sendGpsData = 0;
		if( timeRefType == TIME_SDR24_4800 || timeRefType == TIME_SDR24_9600 )  {
			ClearGpsOut();
		}
		else  {
			if( timeRefType == TIME_SDR24_SKG )
				gpsReset = 1;
			gpsSendState = 1;
			ClearGpsOut();
		}
	}
	else if( cmd == 'V' )  {
		SetVco();
		sendAckFlag = 1;
	}
	else if( cmd == 'r' )  {
		calcFlag = 0;
		sendAdcInfoFlag = 1;
	}
	else if( cmd == 'c' )  {
		calcFlag = 1;
		sendAdcInfoFlag = 1;
	}
	else if( cmd == 'R' )  {
		noDataCounter = 0;
		noDataFlag = 0;
	}
}

void Restart()
{
	hdrStr[0] = 0xaa; hdrStr[1] = 0x55; hdrStr[2] = 0x88; hdrStr[3] = 0x44;
	
	outBuffer = 0;
	txOutCount = 0;
	packetID = 1;
	
	ppsTick = 0;
	gpsTimeOfDay = 0;
	
	gpsLockChar = ggaLockChar = '0';
	gpsSatNum = 0;
	gpsSendState = 0;
	
	secTick = secTickValue = 1600;
	secOffValue = 800;
	
	sampleCount = 0;
	sampleDataLen = 0;
	
	sendTime = 0;
	gpsInCount = gpsQueueInCount = gpsQueueOutCount = newGpsData = 0;
	hdrState = 0;
	gpsBadCount = tx2OutCount = 0;
	gpsReset = 0;
	setGpsTimeFlag = 0;
	gpsWaitLines = 5;
	gpsSendWait = 0;
	sendGpsData = 0;
	echoMode = newEchoChr = 0;
	resetTime = 0;
	sendAckFlag = 0;
	sendLog = 0;
	sendStatus = 0;
	sendAdcInfoFlag = 0;
	gpsTimer = 0;
	noDataCounter = 0;
	needTimeFlag = 0;
	gpsMonth = gpsDay = gpsYear = 0;
			
	ClearGpsOut();
	
	if( ppsHiToLowFlag )  {
		if( !PPS_PIN )
			ppsLowHiFlag = 0;
		else
			ppsLowHiFlag = 1;
	}
	else  {
		if( PPS_PIN )
			ppsLowHiFlag = 0;
		else
			ppsLowHiFlag = 1;
	}
	
	IEC0bits.T1IE = 1;		/* enable interrupts */
	IEC0bits.U1RXIE = 1;

	if( timeRefType )
		InitGps();
}

void Init()
{
	ADCON1bits.ADON = 0;
	ADPCFG = 0xffff;
	TRISA = TRISC = 0;
	
	TRISB = 0x1e0f;
	TRISD = 0x0100;
	TRISF = 0x0010;

	PORTB = ALL_CHAN_OFF;
	PORTF = 0;
	
	TEST_PIN = 0;
	
	RCONbits.SWDTEN = 0;
	
	txOutCount = 0;
	
	TMR1 = 0; 				/* clear timer1 register */
	PR1 = 6143; 			/* set period1 register for 1600 hz with 4.152Mz and 8x PPL */
	T1CONbits.TCS = 0; 		/* set internal clock source */
	IPC0bits.T1IP = 0x06;	/* set priority level */
	IFS0bits.T1IF = 0; 		/* clear interrupt flag */
	T1CONbits.TON = 1; 		/* start the timer */
	SRbits.IPL = 3; 		/* enable CPU priority levels 4-7*/

	timeTick = 0;
	ledPPS = 0;
	numChannels = 1;
	spsRate = 100;
	
	timeRefType = 0;
	ppsHiToLowFlag = 0;
			
	exitLoop = 0;
	DelayMs( 50 );
	newCommandFlag = checkErr = 0;
	goodConfig = 0;
	noWaitFlag = 0;
	gpsSendLine = 0;
	vcoOnTime = 100;
	vcoTime = vcoOffTime = 100;
	vcoPinOn = 0;
	newVcoOnTime = 0;
	newVcoOffTime = 0;
	errWait = spsError = numChanError = 0;
	VCO_OUT = 0;
	watchdogCheck = 0;
	goodChanFlags = 0;
	lastGpsChar = 0;
	skipGpsSend = 0;
	noDataFlag = 0;
}

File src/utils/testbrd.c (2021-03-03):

#include "p30F3014.h"

_FOSC( CSW_FSCM_OFF & XT_PLL8 );
_FWDT( WDT_OFF );
_FBORPOR( PBOR_OFF & BORV_27 & PWRT_16 & MCLR_EN );
_FGS( CODE_PROT_OFF );

#include <uart.h>
#include <stdio.h>

#define MAX_CHANNELS		4
#define SPS					200

#define SPI_LONG_DELAY		5
#define SPI_SHORT_DELAY		3

#define SLONG 				long
#define SINT 				short

#define ULONG				unsigned long
#define WORD				unsigned short
#define BYTE				unsigned char
#define UINT 				unsigned int

#define LED_PIN				LATDbits.LATD2
#define TEST_PIN			LATDbits.LATD9

#define SPI_CLK				LATBbits.LATB8
#define SPI_OUT				LATDbits.LATD0

#define FG_UNIPOLAR_INPUT	0x0008

#define ALL_CHAN_ON 		0x1e00
#define ALL_CHAN_OFF 		0x1ef0
int chanSelect[ MAX_CHANNELS ] = { 0x1ee0, 0x1ed0, 0x1eb0, 0x1e70 };
int chanMask[ MAX_CHANNELS ] = 	 { 0x0001, 0x0002, 0x0004, 0x0008 };

#define SPI_CONF_REG		0x012d
#define SETUP_REG 			0x0000	// 100/120 sps
	
typedef struct  {
	WORD rate;
	WORD sampleTimer;
	BYTE packetsPerSec;
	BYTE frsOn;
	BYTE bits;
} SpsInfo;

SpsInfo spsInfoRun[] = {
	{  15, 107,  5, 0, 0x03 },	
	{  25,  64,  5, 1, 0x02 },	
	{  30,  54, 10, 0, 0x02 },	
	{  50,  32, 10, 1, 0x01 },	
	{  60,  27, 10, 0, 0x01 },	
	{ 100,  16, 10, 1, 0x00 },	
	{ 120,  14, 10, 0, 0x00 },
	{ 200,   8, 10, 1, 0x0c },	
	{   0,   0, 0,  0, 0x00 }		// end	
};

void __attribute__((__interrupt__, no_auto_psv)) _T1Interrupt(void)
{
	IFS0bits.T1IF = 0;		/* clear interrupt flag */
}

void Init()
{
	ADCON1bits.ADON = 0;
	ADPCFG = 0xffff;
	TRISA = TRISC = 0;
	
	TRISB = 0x0e0f;
	
	TRISD = 0x0100;
	TRISF = 0x0010;

	PORTB = ALL_CHAN_OFF;
	PORTF = 0;
	
	TEST_PIN = 0;
	
	TMR1 = 0; 				/* clear timer1 register */
	PR1 = 1535; 			/* set period1 register */
	T1CONbits.TCS = 0; 		/* set internal clock source */
	IPC0bits.T1IP = 0x06;	/* set priority level */
	IFS0bits.T1IF = 0; 		/* clear interrupt flag */
	T1CONbits.TON = 1; 		/* start the timer */
	SRbits.IPL = 3; 		/* enable CPU priority levels 4-7*/
}

void DelayMs( int ms )
{
	int i;
	long delay;
	
	for( i = 0; i != ms; i++ )  {
		delay = 1625L;
		while( delay-- );
	}
}

void SetBaudRate( int setInt )
{
	WORD div, c1, c2, data;
	
	div = 15;					// 38.4k baud @ 4.912Mhz * 8x PLL
	
	IEC0bits.U1TXIE = 0;
	IEC0bits.U1RXIE = 0;
	CloseUART1();
	
	c1 = UART_EN & UART_IDLE_CON & UART_DIS_WAKE & UART_DIS_LOOPBACK &
	    	UART_DIS_ABAUD & UART_NO_PAR_8BIT &	UART_1STOPBIT;
	c2 = UART_TX_PIN_NORMAL & UART_TX_ENABLE & UART_ADR_DETECT_DIS & 
		UART_RX_OVERRUN_CLEAR;
	OpenUART1( c1, c2, div  );
	
	if ( U1STAbits.OERR )
		U1STAbits.OERR = 0;
	
	data = U1STA;
	data &= 0xff3f;
	U1STA = data;
}

int IsCS5532DataRdy( int chan )
{
	if( PORTB & chanMask[ chan ] )
		return 0;
	return 1;
}

// Delay for SPI R/W
void SPIDly( int cnt )
{
	while( cnt-- )
		asm ("NOP");
}

void WriteSPIByte( BYTE data )
{
	int cnt = 8;
		
	while( cnt-- )  {
		if( data & 0x80 )
			SPI_OUT = 1;
		else
			SPI_OUT = 0;
		SPIDly( SPI_LONG_DELAY );
		SPI_CLK = 1;
	    data <<= 1;
		SPIDly( SPI_SHORT_DELAY );
    	SPI_CLK = 0;
	}
}

void WriteRegister( BYTE cmd, ULONG data )
{
	BYTE *p = (BYTE *)&data;
	WriteSPIByte( cmd );
	WriteSPIByte( p[3] );
	WriteSPIByte( p[2] );
	WriteSPIByte( p[1] );
	WriteSPIByte( p[0] );
}

BYTE ReadSPIByte( int chan )
{
	BYTE data = 0;
	int cnt = 8;
	while( cnt-- )  {
		data <<= 1;
		SPI_CLK = 1;
		SPIDly( SPI_LONG_DELAY );
		if( PORTB & chanMask[ chan ] ) 
			data |= 1;
		SPIDly( SPI_SHORT_DELAY );
		SPI_CLK = 0;
		SPIDly( SPI_LONG_DELAY );
  	}
	return data;
}
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
